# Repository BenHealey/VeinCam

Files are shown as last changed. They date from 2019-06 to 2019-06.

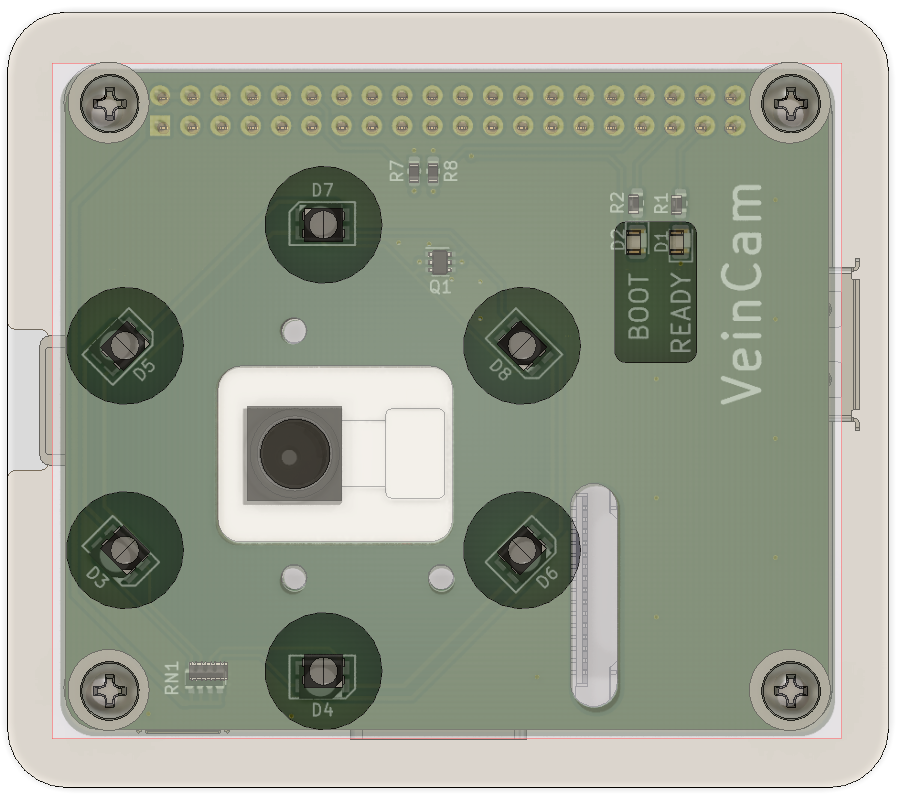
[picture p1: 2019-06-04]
Hardware/ProductionOutputs/Renders/topWithOverlay.PNG

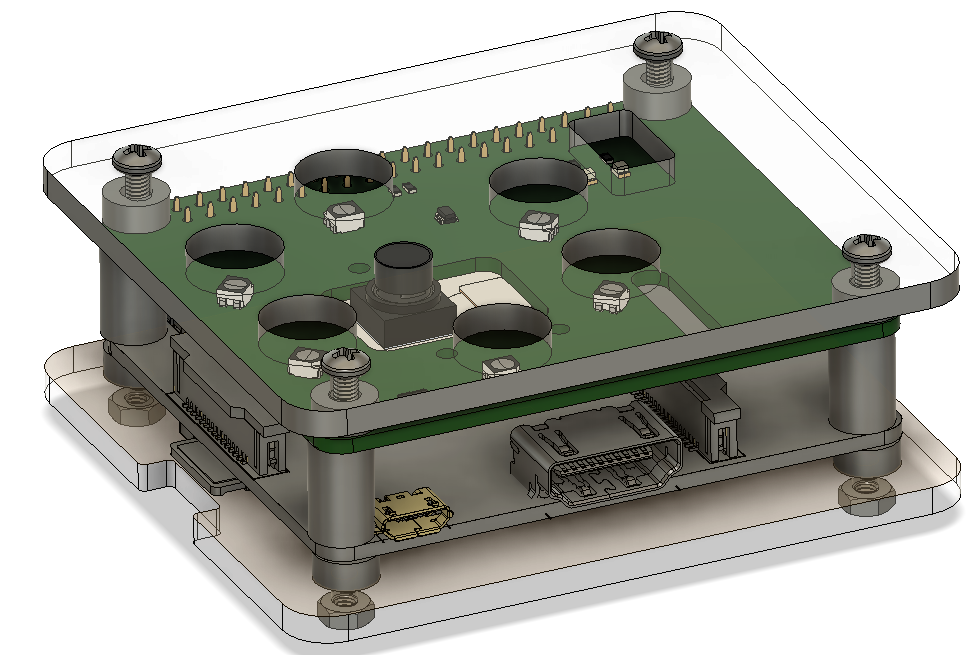
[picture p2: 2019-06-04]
Hardware/ProductionOutputs/Renders/side.PNG

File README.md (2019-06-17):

# VeinCam

VeinCam is an educational tool for vein visualisation. It uses near infrared (nIR) light and a nIR-sensitive camera to stream a real-time vein-enhanced video image to a user's phone or tablet. In addition to a custom PCB to control the nIR light source, the device employs widely available low-cost components from the [Raspberry Pi educational foundation](https://www.raspberrypi.org/).

VeinCam is *not* a certified medical device and is therefore not intended for use in a clinical setting.

---
## Contents
1. [Development History](###1-development-history)
2. [Structure of the Repository](###2-structure-of-the-repository)
3. [Hardware Kit](###3-hardware-kit)

---
### 1. Development History
Much of VeinCam's development occurred during [ANU Engineering](https://cs.anu.edu.au/TechLauncher/) capstone projects in 2018 and 2019. Created as an open-source project, anyone who may find VeinCam useful for learning can get the information necessary to make one for their own personal use in this GitHub repository.

### 2. Structure of the Repository
The repository is broadly split into Hardware and Software sections.

Each section contains schematics or code for the components of the device. The root folders for each section contain *readme* files outlining their contents and key aspects of functionality. The *assembly* instructions in each folder outline at a high level how to get the device working.

Please note that while the software licence is GPL3.0, the hardware specifications are intended to be available for personal non-commercial use one. Only the developers may create commercial versions of the VeinCam hardware for sale to others.

### 3. Hardware Kit
Many people will not have access to the equipment required to make the hardware components of the device, so we are in the process of finalising a low-cost kit you can purchase. (due end of 2019)

You can check availability at the [VeinCam Hardware Kit website](https://veincam.com/).

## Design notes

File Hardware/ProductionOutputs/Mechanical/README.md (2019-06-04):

## NOTE
We are relying on the draft angle from the laser cutter to hold the lens in. Different lasers/lenses/focal lengths will alter this draft angle and this needs to be taken into account.  

We also needed to flip the top acrylic to ensure that the lens would not fall out, as by default the lens was pushed in from the front. 

The dimensions may also need to be altered depending on how wide the laser cuts.

Any questions ask Josh, easier to explain with a VeinCam in hand and in person.

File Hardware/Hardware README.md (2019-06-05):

## What is in the Hardware Folder?

* **Library** Contains relavent KiCad library files for the boards. 
* **Production Outputs** Are the files you can use to produce VeinCam.
* **VeinCamHat** Contains the KiCad files for the RPi 3A+ model of the VeinCam. Also contains a render of the PCA. 
* **ReadmeHW** Is the document you are reading right now.

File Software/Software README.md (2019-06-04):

## app.py Functionality

### What Does it Do?
When this script is run it initially does two things: turns the 'ready' LED on and starts the server, subsequently if the server is ever exited, the ready LED is turned off. Other than that app.py contains many important function definitions including:
* Updating the settings and statistics dictionaries
* Global Flask server render template
* LED declarations and updating functions
* Camera setting altering functions
* The server shutdown function
* Flask routing functions for:
    * Shutting the server down
    * Altering a camera setting
    * Refreshing the Pi Statistics
    * Starting the video feed
* Main video feed loop (generator function)

The names and briefly the ways in which each of these functions work are explained below:

### Functions Breakdown

#### update_settings_cache
Updates the dictionary entry for the corresponding attribute and updates the whole json settings file with the correct formatting

#### update_system_stats
Updates the statistics cache with the new cpu usage, cpu temperature and ram usage, as well accounts for errors temperature reading. This uses the module: psutil

#### index
(Flask routing function)Performs an initial statistics update and defines the global Flask server render template (being: index.html). Note: this is a routing function and is called the moment the web page is opened

#### all_led_off
Turns all LEDs off by writing 0 (positive logic)

#### alter_light_level
Updates the physical voltage applied to the LEDs based on a maximum duty cycle at a refresh rate of 750Hz or turns the LEDs off if the light level value is 0. For both these cases the settings cache is updated (call to function)

#### alter_cam_setting
updates the settings cache (call to function) based on the attribute being changed, e.g. if it was the light level then the alter_light_level function also needs to be called

#### shutdown_server
Shuts down the Flask server, raises a runtime error if not able to do so

#### shut_server
(Flask routing function) Turns all LEDs off when server needs to be shutdown and calls the shutdown_server function

#### alter_config
(Flask routing function) Requests the attribute and value that needs to be changed and calls alter_cam_setting using these values

#### refresh_stats
(Flask routing function) Makes a call to update_system_stats when this was requested on server side

#### gen(camera)
Defines the main generator loop that grabs processed frames from the other script. Makes a call to get_frame from camera_piopencv.py and yields it in the correct format for HTML

#### video_feed
(Flask routing function) Gets called when the user turns the camera on in the UI. Initialises the camera class from camera_piopencv.py with the current setting cache and using it makes a call to the gen(camera) function

## camera_piopencv.py Functionality

### What Does it Do?
This script does not run anything when called, as it only contains three classes all used to obtain and process frames from the camera. 

The first of these classes is essentially a general purpose event class that wait for events, set events adn clear events. This class is used so that app.py is essentially only ever attempting to get new processed images as fast as they are being returned so that the raspberry pi isn't working any harder than it should

The second of these classes simply defines how the MJPEG output bytes stream of the camera when recording should split and store each frame

The third and most important class in this script defines and calculates camera values, describes how camera settings are updated from the settings cache, runs a thread that searches for new frames and sets an event, and sets up the raspberry pi camera to grab frames, process them and send them to the Flask server in the correct format.

The names and briefly the ways in which each of the functions within these classes work are described below:

### Functions Breakdown

#### CameraEvent Class
##### init
* Sets up the events dictionary
##### wait
* Waits for an event to be set before moving on
##### set
* Sets an event (called by the _thread function)
##### clear
* Clears any set events

#### StreamOutput Class
##### init
* Sets up frame and stream variables (Note that stream will be a bytes class, and frame will be a string class)
##### write
* Defines how the MJPEG stream is written the stream variable. Each time it is written this function checks if the stream starts with the hexadecimal value of FFD8, which indicates the start of a new frame. If this happens the reference point is set to the start of the stream, frame is set to the string value of the stream, the stream is truncated and the reference point is reset.
#### Camera Class
##### init
* sets up the camera settings as the current setting cache, sets up the crop and roi sizes using the crop_size function, and starts the camera thread (_thread)
##### crop_size
* Calculates the 4 pixel locations of the crop and roi sizes then appends them to a list and returns the list
##### update_settings
* updates the roi and contrast settings of the camera if they have changed in the settings cache
##### get_frame
* This is function called by app.py in its main video feed generator loop. It simply calls wait and clear to make sure a new frame is ready the returns the new frame
##### _thread
* This sets up the frames function as a generator loop and and calls the set function whenever a new frame is ready. The thread will break if the camera is turned off on the server side.
##### frames
* The main function that obtains the initial image. The raspberry pi camera is initialised and depending on what type of image capture technique the user has selected, the function will either:
    * Start a MJPEG recording and write to the StreamOutput Class, the frame variable in that class is converted to an array, then to an image, passed to the image_processing function and encoded back to bytes
    * Or start a YUV continuous image capture, write to a vector array variable, reshape the vector to an image array, pass it to the image_processing function and encode it back to bytes
##### image_processing
* This function takes in an image and does the following things in this order:
    * Crops the input image depending on crop values set in init
    * Creates a copy of the cropped image (final image)
    * If ROI is selected in UI (and subsequently in the settings cache):
        * Creates a new array that is the region of interest crop (If roi is selected)
        * Creates a histogram_equalisation
        * If the colour setting is applied:
            * Converts the roi image to LAB
            * Splits up the channels into L, A and B
            * Applies the histogram equalisation to the L channel
            * Merges the Channels together
        * If the colour setting is not applied:
            * Applies histogram to the roi image
        * Sets the roi portion of the final image (copy) to the applied histogram equalisation

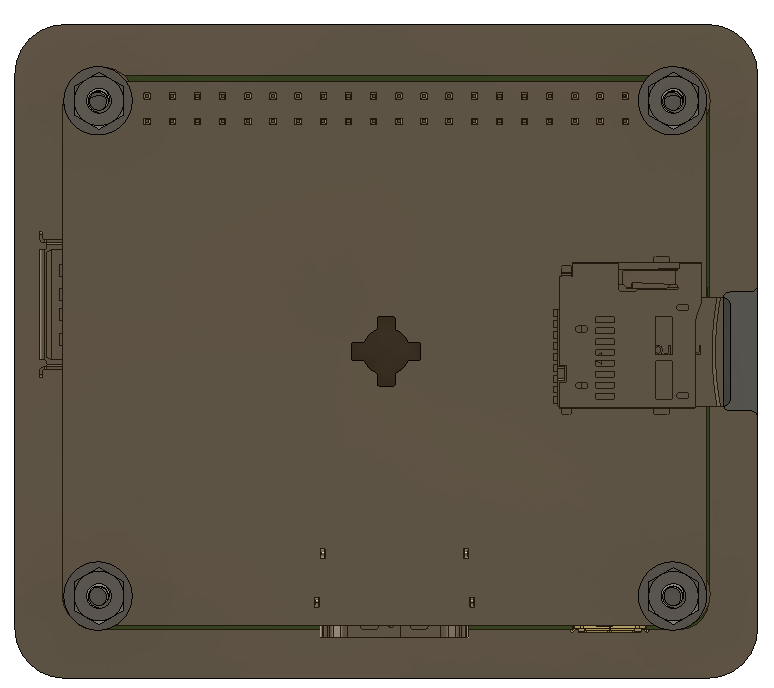
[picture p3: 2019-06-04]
Hardware/ProductionOutputs/Renders/bottom.PNG

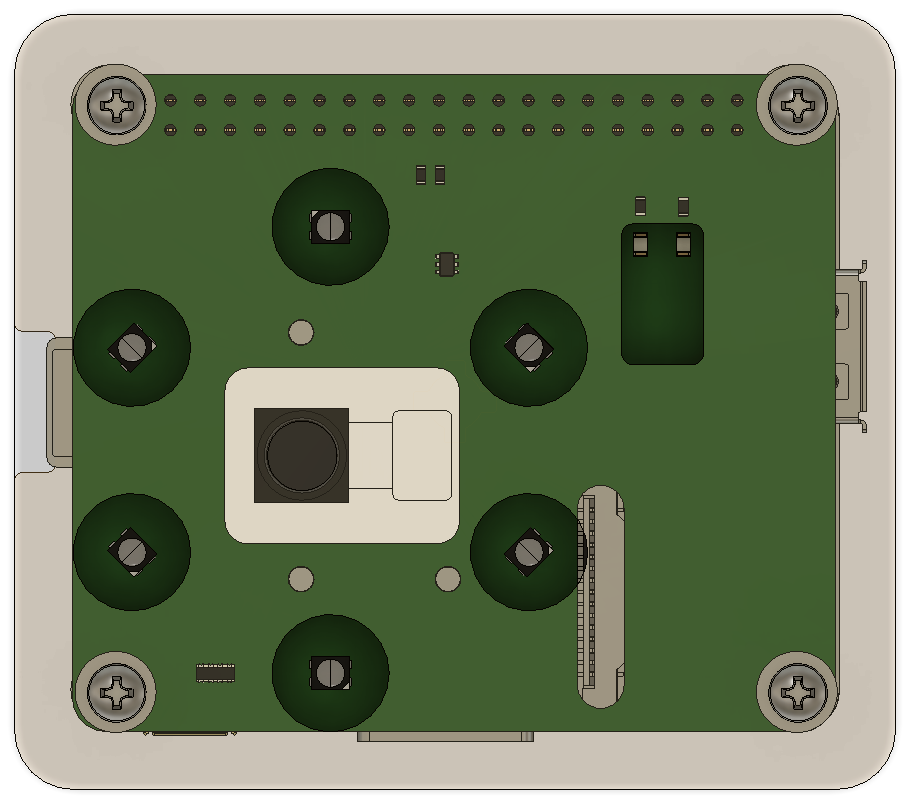
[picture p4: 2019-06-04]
Hardware/ProductionOutputs/Renders/top.PNG

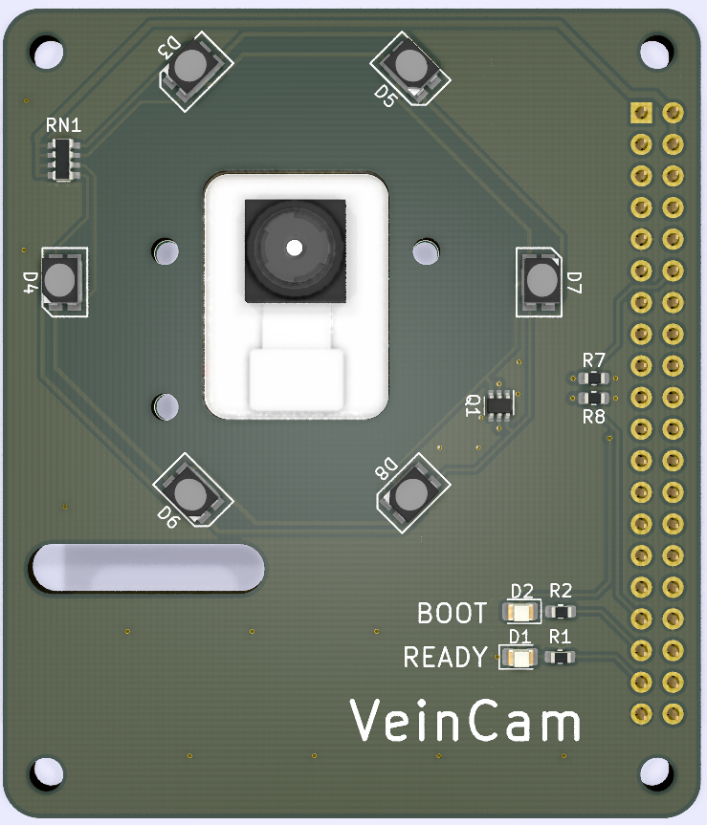
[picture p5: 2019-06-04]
Hardware/ProductionOutputs/Renders/PCB.PNG

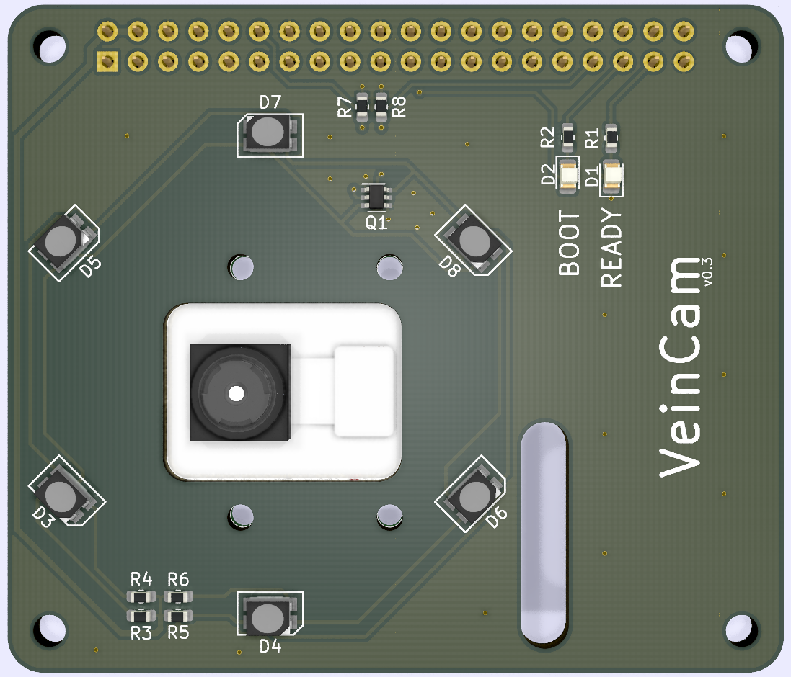
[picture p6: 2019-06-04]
Hardware/VeinCamHat/Render.png

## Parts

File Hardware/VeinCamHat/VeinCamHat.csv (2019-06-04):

Source: | C:\Users\Josh Johnson\Dropbox\ENGN4221\veincam2019\Hardware\VeinCamHat\VeinCamHat.sch
Date: | 26/05/2019 19:16
Tool: | Eeschema (5.1.2)-1
Generator: | C:\Program Files\KiCad\bin\scripting\plugins/bom_csv_grouped_by_value.py
Component Count: | 19
Individual Components:
Item | Qty | Reference(s) | Value | LibPart | Footprint | Datasheet
 |  | D1 | GREEN LED | Device:LED | LED_SMD:LED_0805_2012Metric | ~
 |  | D2 | RED LED | Device:LED | LED_SMD:LED_0805_2012Metric | ~
 |  | D3 | SFH7252 | VeinCam_Symbols:SFH7252 | VeinCam_Footprints:SFH7252 | ~
 |  | D4 | SFH7252 | VeinCam_Symbols:SFH7252 | VeinCam_Footprints:SFH7252 | ~
 |  | D5 | SFH7252 | VeinCam_Symbols:SFH7252 | VeinCam_Footprints:SFH7252 | ~
 |  | D6 | SFH7252 | VeinCam_Symbols:SFH7252 | VeinCam_Footprints:SFH7252 | ~
 |  | D7 | SFH7252 | VeinCam_Symbols:SFH7252 | VeinCam_Footprints:SFH7252 | ~
 |  | D8 | SFH7252 | VeinCam_Symbols:SFH7252 | VeinCam_Footprints:SFH7252 | ~
 |  | H1 | MountingHole | Mechanical:MountingHole | MountingHole:MountingHole_2.7mm_M2.5 | ~
 |  | H2 | MountingHole | Mechanical:MountingHole | MountingHole:MountingHole_2.7mm_M2.5 | ~
 |  | H3 | MountingHole | Mechanical:MountingHole | MountingHole:MountingHole_2.7mm_M2.5 | ~
 |  | H4 | MountingHole | Mechanical:MountingHole | MountingHole:MountingHole_2.7mm_M2.5 | ~
 |  | J1 | Raspberry_Pi_2_3 | Connector:Raspberry_Pi_2_3 | Connector_PinSocket_2.54mm:PinSocket_2x20_P2.54mm_Vertical | https://www.raspberrypi.org/documentation/hardware/raspberrypi/schematics/rpi_SCH_3bplus_1p0_reduced.pdf
 |  | Q1 | NTJD4001N | VeinCam_Symbols:NTJD4001N | Package_TO_SOT_SMD:SOT-363_SC-70-6
 |  | R1 | 1K | Device:R | Resistor_SMD:R_0603_1608Metric | ~
 |  | R2 | 1K5 | Device:R | Resistor_SMD:R_0603_1608Metric | ~
 |  | R7 | 10K | Device:R | Resistor_SMD:R_0603_1608Metric | ~
 |  | R8 | 10K | Device:R | Resistor_SMD:R_0603_1608Metric | ~
 |  | RN1 | R_Pack04 | Device:R_Pack04 | Resistor_SMD:R_Array_Concave_4x0603 | ~
Collated Components:
Item | Qty | Reference(s) | Value | LibPart | Footprint | Datasheet
1 | 1 | D1 | GREEN LED | Device:LED | LED_SMD:LED_0805_2012Metric | ~
2 | 1 | D2 | RED LED | Device:LED | LED_SMD:LED_0805_2012Metric | ~
3 | 6 | D3, D4, D5, D6, D7, D8 | SFH7252 | VeinCam_Symbols:SFH7252 | VeinCam_Footprints:SFH7252 | ~
4 | 4 | H1, H2, H3, H4 | MountingHole | Mechanical:MountingHole | MountingHole:MountingHole_2.7mm_M2.5 | ~
5 | 1 | J1 | Raspberry_Pi_2_3 | Connector:Raspberry_Pi_2_3 | Connector_PinSocket_2.54mm:PinSocket_2x20_P2.54mm_Vertical | https://www.raspberrypi.org/documentation/hardware/raspberrypi/schematics/rpi_SCH_3bplus_1p0_reduced.pdf
6 | 1 | Q1 | NTJD4001N | VeinCam_Symbols:NTJD4001N | Package_TO_SOT_SMD:SOT-363_SC-70-6
7 | 1 | R1 | 1K | Device:R | Resistor_SMD:R_0603_1608Metric | ~
8 | 1 | R2 | 1K5 | Device:R | Resistor_SMD:R_0603_1608Metric | ~
9 | 2 | R7, R8 | 10K | Device:R | Resistor_SMD:R_0603_1608Metric | ~
10 | 1 | RN1 | R_Pack04 | Device:R_Pack04 | Resistor_SMD:R_Array_Concave_4x0603 | ~

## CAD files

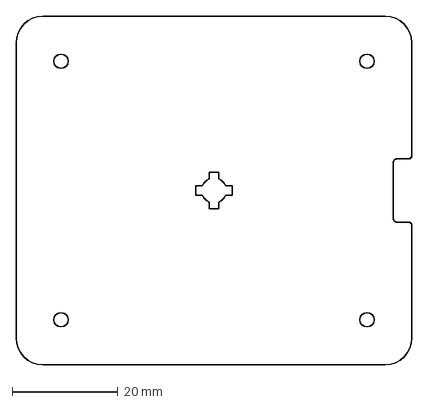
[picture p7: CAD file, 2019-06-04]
Hardware/ProductionOutputs/Mechanical/bottomCase.dxf
75.0 x 66.0 mm

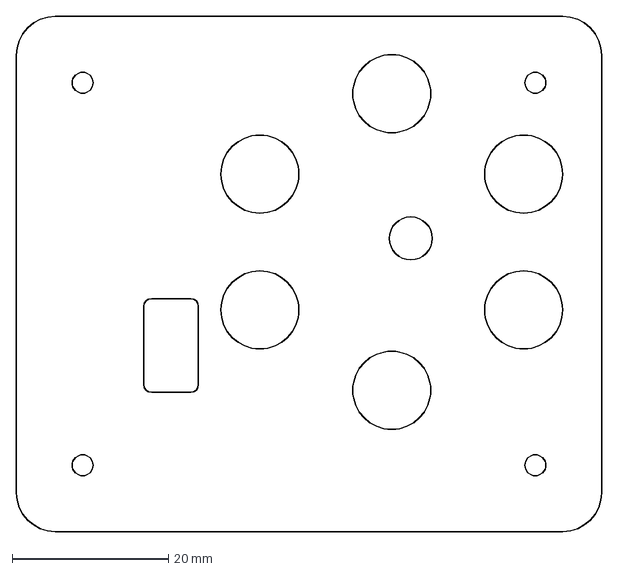
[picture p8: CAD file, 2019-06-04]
Hardware/ProductionOutputs/Mechanical/topCase.dxf
75.0 x 66.0 mm

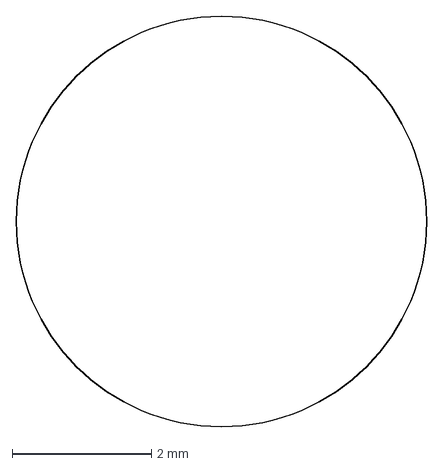
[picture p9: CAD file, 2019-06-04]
Hardware/ProductionOutputs/Mechanical/lens.dxf
5.90 x 5.90 mm

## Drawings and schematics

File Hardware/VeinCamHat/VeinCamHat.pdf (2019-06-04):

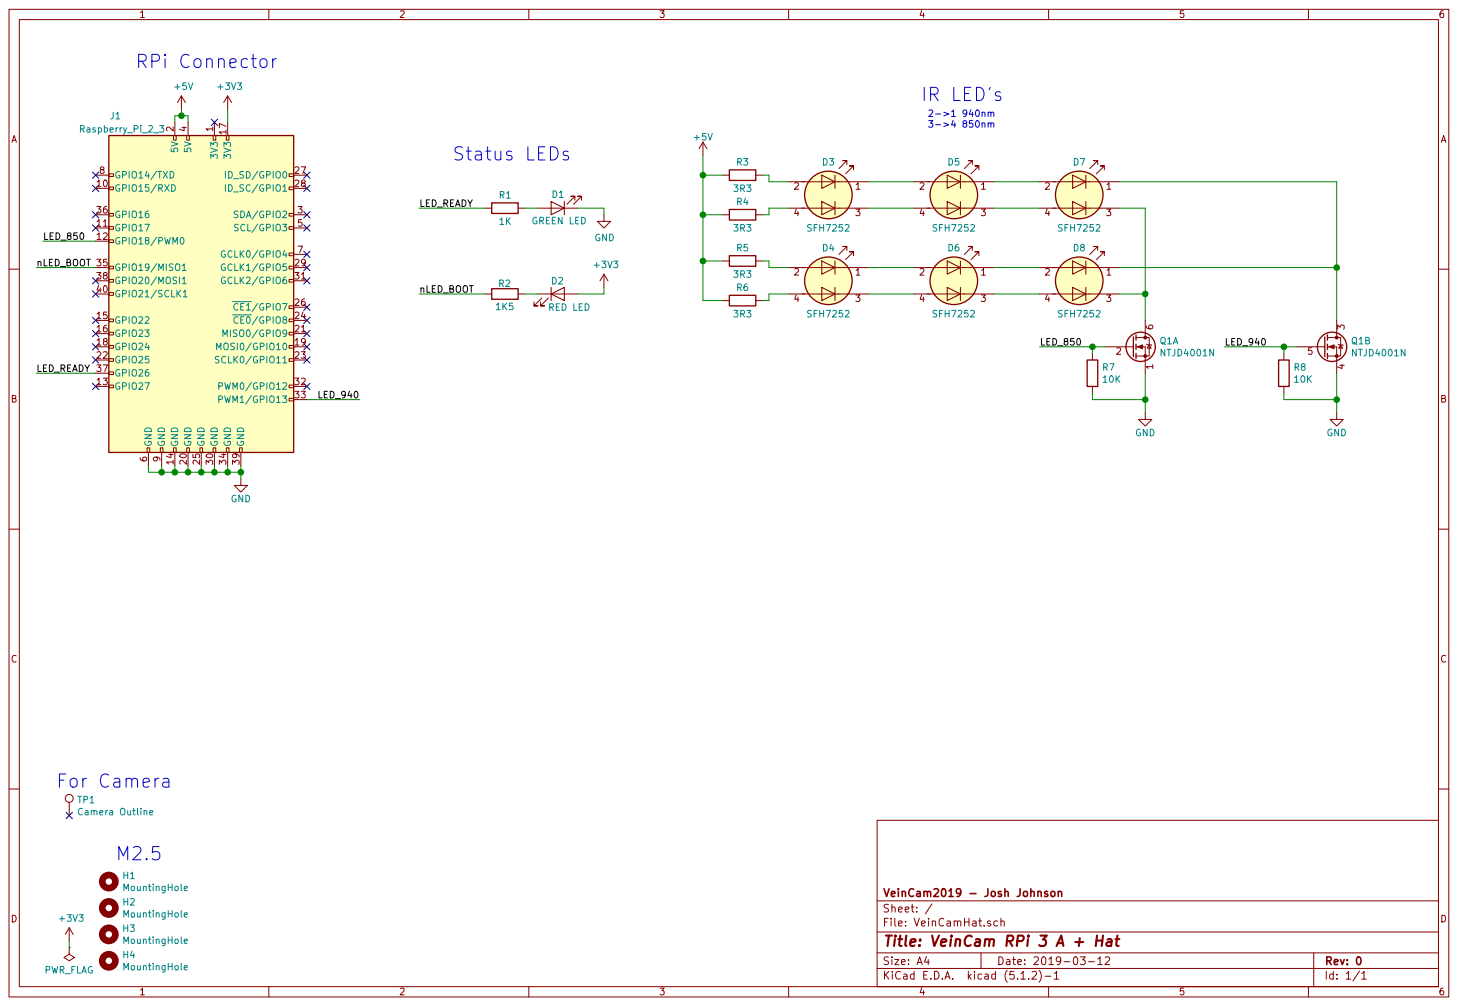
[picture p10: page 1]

Id: 1/1 Title: VeinCam RPi 3 A + Hat File: VeinCamHat.sch Sheet: / VeinCam2019 - Josh Johnson RPi Connector

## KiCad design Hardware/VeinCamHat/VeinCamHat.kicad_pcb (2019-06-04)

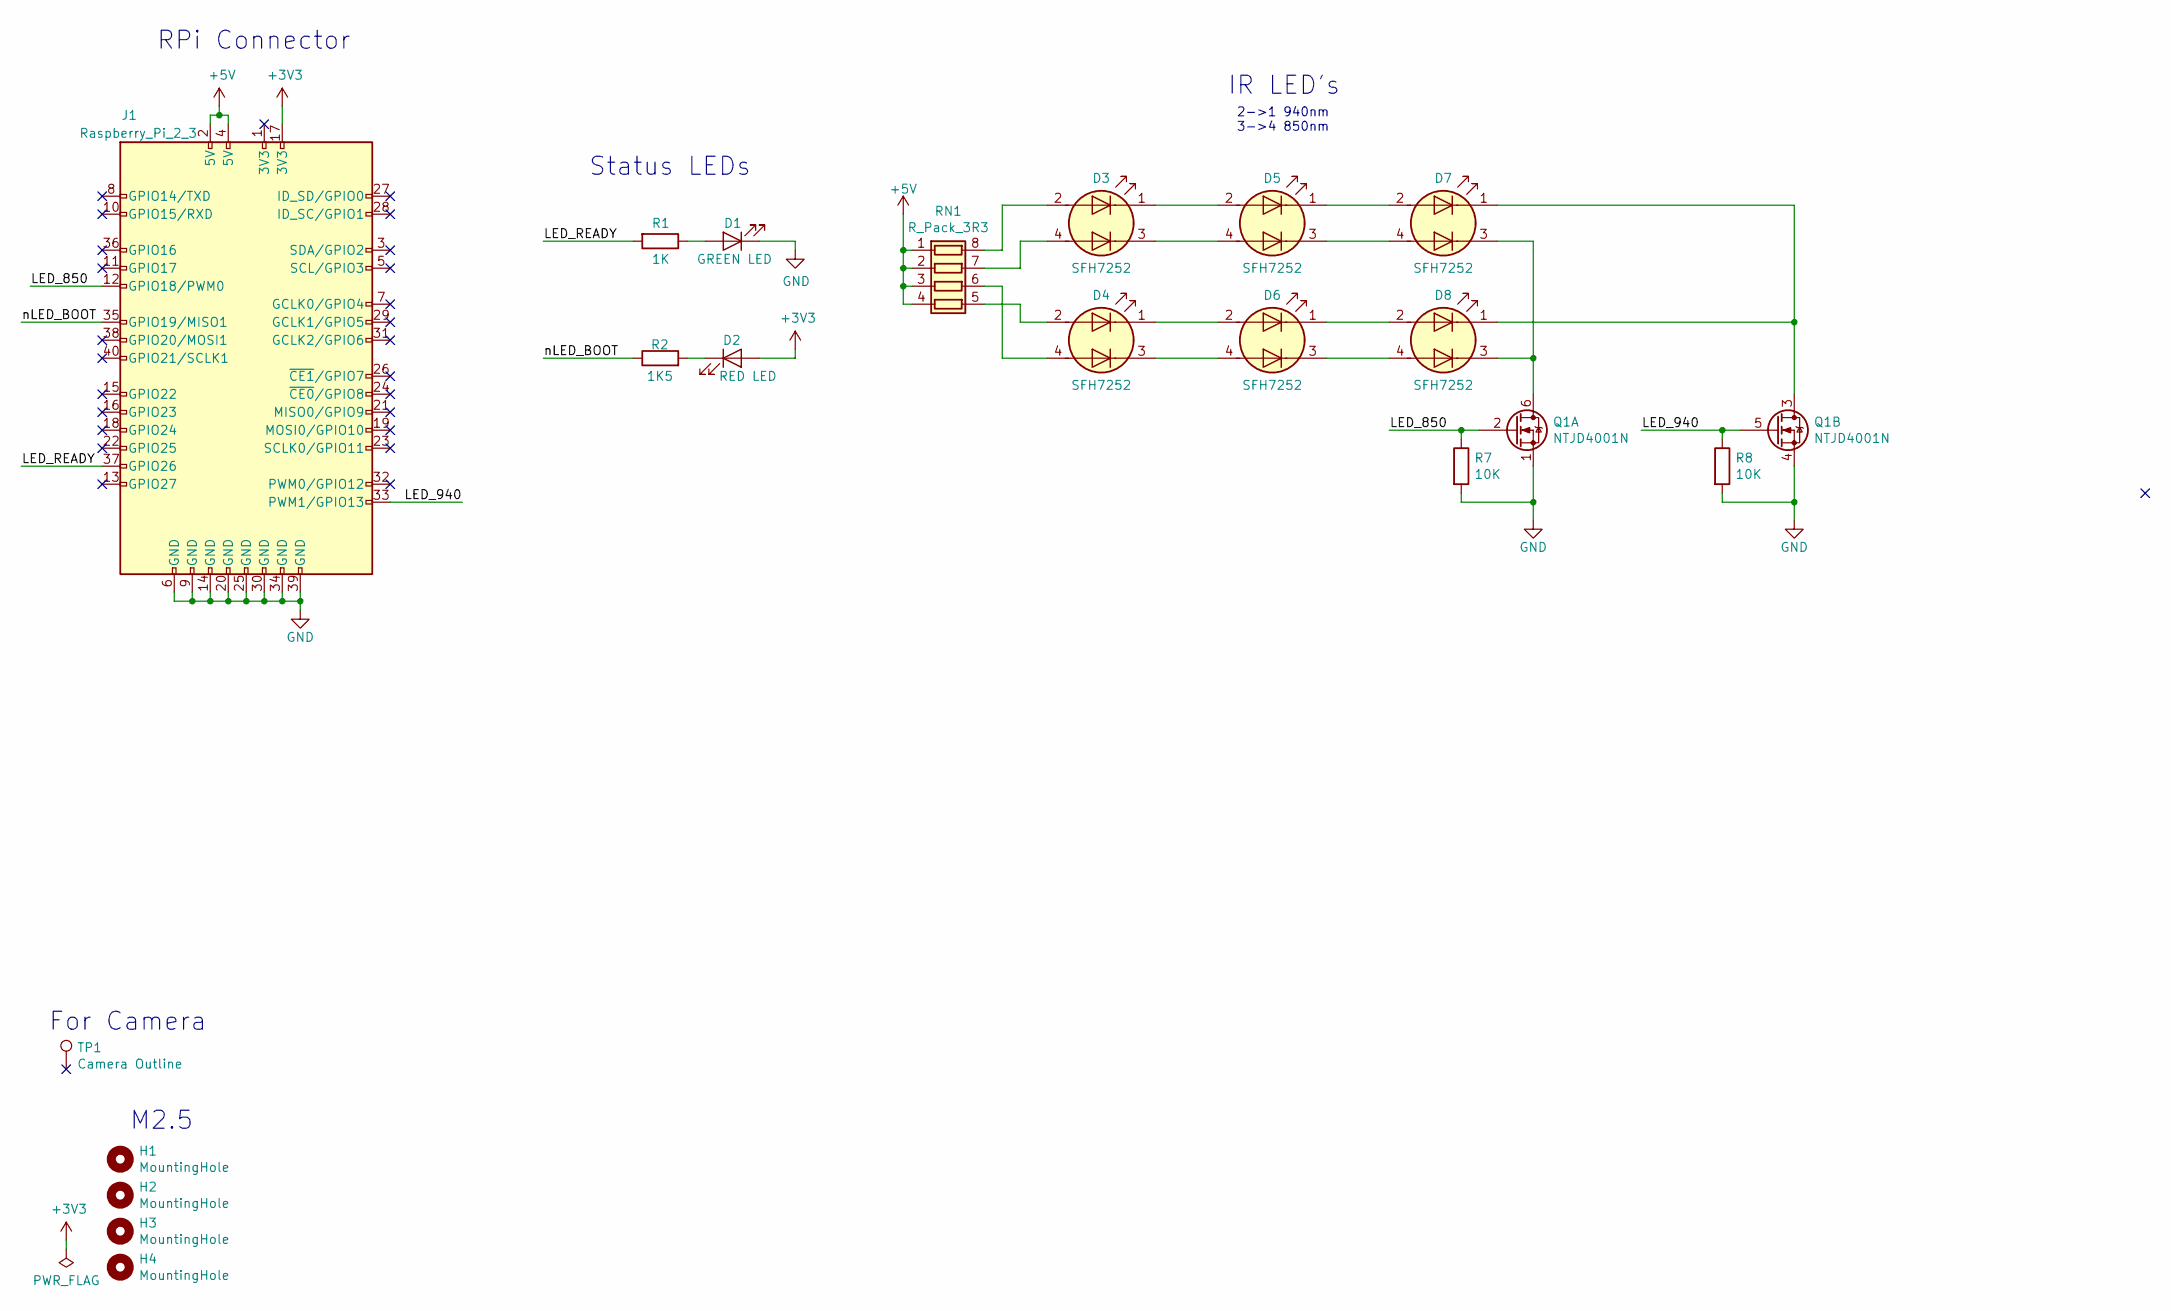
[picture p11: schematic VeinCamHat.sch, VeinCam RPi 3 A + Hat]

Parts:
D1: GREEN LED; LED_0805_2012Metric
D2: RED LED; LED_0805_2012Metric
D3, D4, D5, D6, D7, D8: SFH7252
H1, H2, H3, H4: MountingHole; MountingHole_2.7mm_M2.5
J1: Raspberry_Pi_2_3; PinSocket_2x20_P2.54mm_Vertical
Q1: NTJD4001N; SOT-363_SC-70-6
R1: 1K; R_0603_1608Metric
R2: 1K5; R_0603_1608Metric
R7, R8: 10K; R_0603_1608Metric
RN1: R_Pack_3R3; R_Array_Convex_4x0603
TP1: Camera Outline; PiCamera

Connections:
+3V3: D2.2 (A), J1.17 (3V3)
+5V: J1.2 (5V), J1.4 (5V), RN1.1 (R1.1), RN1.2 (R2.1), RN1.3 (R3.1), RN1.4 (R4.1)
/LED_850: J1.12 (GPIO18/PWM0), Q1.2 (G), R7.1
/LED_940: J1.33 (PWM1/GPIO13), Q1.5 (G), R8.1
/LED_READY: J1.37 (GPIO26), R1.2
/nLED_BOOT: J1.35 (GPIO19/MISO1), R2.1
GND: D1.1 (K), J1.6 (GND), J1.9 (GND), J1.14 (GND), J1.20 (GND), J1.25 (GND), J1.30 (GND), J1.34 (GND), J1.39 (GND), Q1.1 (S), Q1.4 (S), R7.2, R8.2
unnamed: D1.2 (A), R1.1
unnamed: D2.1 (K), R2.2
unnamed: D3.1 (K2), D5.2 (A2)
unnamed: D3.2 (A2), RN1.8 (R1.2)
unnamed: D3.3 (K1), D5.4 (A1)
unnamed: D3.4 (A1), RN1.7 (R2.2)
unnamed: D4.1 (K2), D6.2 (A2)
unnamed: D4.2 (A2), RN1.5 (R4.2)
unnamed: D4.3 (K1), D6.4 (A1)
unnamed: D4.4 (A1), RN1.6 (R3.2)
unnamed: D5.1 (K2), D7.2 (A2)
unnamed: D5.3 (K1), D7.4 (A1)
unnamed: D6.1 (K2), D8.2 (A2)
unnamed: D6.3 (K1), D8.4 (A1)
unnamed: D7.1 (K2), D8.1 (K2), Q1.3 (D)
unnamed: D7.3 (K1), D8.3 (K1), Q1.6 (D)

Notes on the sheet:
RPi Connector
M2.5
IR LED's
2->1 940nm 3->4 850nm
Status LEDs
For Camera

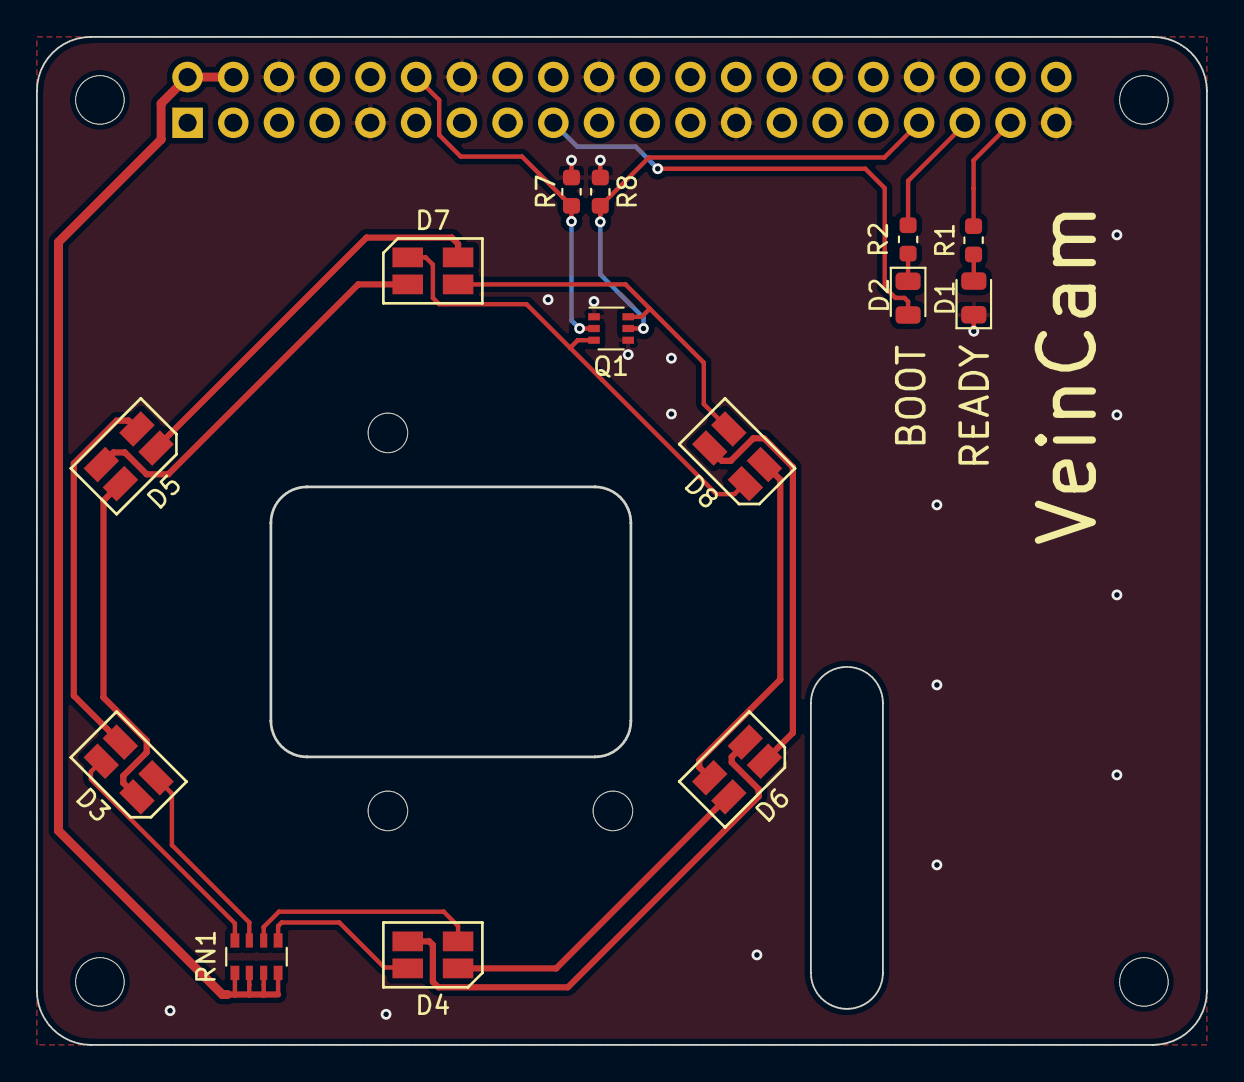
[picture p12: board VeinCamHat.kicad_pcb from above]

Board: 2 copper layers, 65.0 x 56.0 mm, 20 parts (1 on the bottom side), 23 nets.

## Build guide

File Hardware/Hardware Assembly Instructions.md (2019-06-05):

# Assembly Instructions

### Hardware
* Using the M2 screws, attach the NoIR Camera on the underside of the VeinCam hat. 
* Plug the flat flex cable into the camera connector on the Raspberry Pi.
* Connect the VeinCam hat to the Raspberry Pi, ensuring that the flat flex cable does not get pinched. The cable routing is not ideal, but it will all fit inbetween the two boards. 
* Follow the [Software](#Software) instructions to get the board up and running. This is required before continuing assembly as the cameras focus cannot be changed after assembly.
* Using the cross shaped cutout on the VeinCam back panel, adjust the focus ring on the camera until objects 20-30cm away from the lens are in focus. It may be required to use pliers or tweezers to initially move the focus ring, however once it is loose the provided tool can be used. 
* Insert the IR filter into the small cutout on the front acrylic panel. It will only go in from the back side of the acrylic, so if it does not fit try flipping the parts around until they fit. 
* Place the M2.5 screws through the front panel and place on the table top down. Slide 3mm spacers over the screws, one per screw.
* Position the 11mm spacers between the VeinCam hat and the Raspberry PI. Locate the holes in the VeinCam hat over the M2.5 screws and slide into position. May require moving the 11mm spacers until they line up with the holes. 
* Place the remaining 3mm spacers on top of the Raspberry Pi. Install the rear acrylic with the SD card cutout located over the SD card, and install the M2.5 nuts. Using a phillips head screwdriver tighted the screws until snug. 
* Congratulations, you can now look at your veins!

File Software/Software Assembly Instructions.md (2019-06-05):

# Assembly Instructions

### Software

#### Connecting to the pi

* Apply power to the raspberry pi through the USB power port
* Wait for the pi to boot, indicated by the 'ready' LED
* Connect to the pi's wifi network on the chosen device
* Connect to the VeinCam server through a web browser on the chosen device
* Press the 'on' switch to activate the camera  

#### Changing the user parameters 

* To change the base URL: 
    - Change the `10.0.0.5` variable in the autohotspot launch script

* To change the wifi name:
    - ssh into the pi 
    - Run: `cd /etc/`
    - Run: `nano hostname`
    - Change the host name
    - When finished press `ctrl + x`, `Y`, `Enter`

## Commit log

2018-12-18 Initial transfer from ENG4221 project repo
    [Casing-v2.1-shell.stl, Casing-v2.1lid.stl, Casing-v2.2 Lid.stl, Casing-v2.2 Shell.stl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]
2019-06-04 Clearing repo in advance of 2019 update
    [Casing-v2.1-shell.stl, Casing-v2.1lid.stl, Casing-v2.2 Lid.stl, Casing-v2.2 Shell.stl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]
2019-06-04 Initial update from 2019 project
    [VeinCamHat-B_Cu.gbr, VeinCamHat-B_Mask.gbr, VeinCamHat-B_SilkS.gbr, VeinCamHat-Edge_Cuts.gbr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]
2019-06-05 Adding assembly instructions. Minor typo edits elsewhere.
2019-06-12 Temporary buttons to test CLAHE filtering settings.
